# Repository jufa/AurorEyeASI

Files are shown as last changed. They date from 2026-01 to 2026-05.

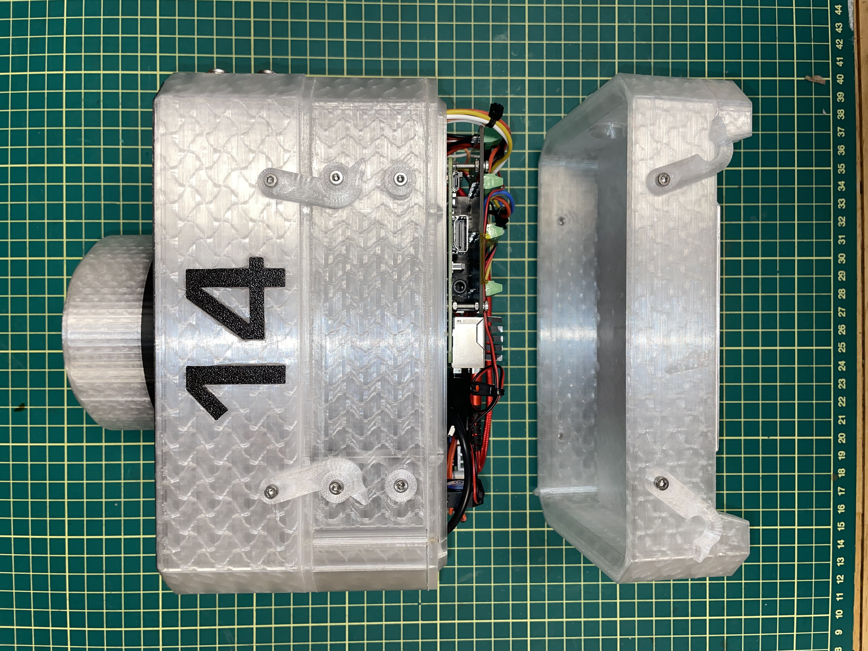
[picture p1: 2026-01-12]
BuildReferencePhotos/IMG_7756.jpg

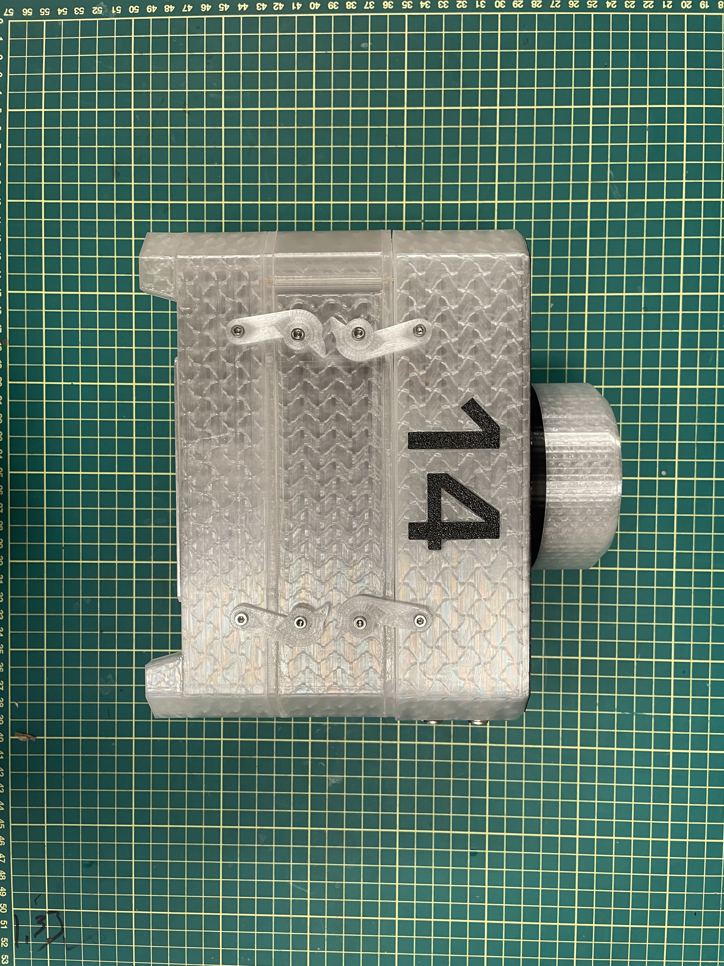
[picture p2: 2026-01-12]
BuildReferencePhotos/IMG_7746.jpg

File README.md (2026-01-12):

# AurorEyeASI
see [AurorEye.ca](https://auroreye.ca)

## Contact
jeremy@jufaintermedia.com or in this repository as an issue

## Terms of Use
Please see LICENSE.md

## Warranty
Please see LICENSE.md

### Bill of Materials
Please see BOM.md

## 3D Printable Shell
This repository includes an .3mf file for 3D printing. Preferred material is PETG.

## Development projects for students, researchers
### Hardware
* Low temperature tolerant LiFePO4 battery pack characterization
* Updates to KiCAD design files for Pi “HAT” circuit board
* Manufacturability considerations (maybe 3D printed internal frame for sensor alignment and support)
* Heat flow/moisture characterization and management (dew point, built-in heaters, condensation prevention for longer periods of deployment)
* 3D printed shell with in-built insulative properties, stackable, modular (in progress now)

### Optics and Sensor Characterization
* Optical characterization (lens, camera, distortion and light falloff parameters)
* Image file transforms (Camera internal color and post processing characterization)
* possible calibration with distortion from a weather cover dome

### Comms and UI
* Test with satellite or cellular Wifi
* Modify cloud upload for appropriate cloud environment (right now it is google cloud)
* UI development (currently a web app which provides flexibility as well as onboard buttons and display)
* Improvements or characterization of camera communication using established open source library (gPhoto2)

### Software/Firmware
* Onboard firmware updates, (branches off of main github repository with new features)
* Post processing tools updates (OpenCV, Python, Davinci Resolve Fusion workflows)
* Archiving, storing, and sharing system website (currently youtube and local backup servers of still image sequences)

### Skill areas for students
* Batteries and power electronics
* Temperature management hardware and sensing
* Magnetometers, Accelerometers for alignment
* Python programming
* Cloud API interface
* GitHub software collaboration
* Image processing and characterization using OpenCV or other open tools
* Image recognition/Machine Learning/AI
* 3D CAD/CAM
* Web Application development
* Video editing for outreach
* Field work campaigning and collaboration between multiple instruments
* Fabrication with Aluminum and Plastic
* Electronics assembly, packaging for harsh environments

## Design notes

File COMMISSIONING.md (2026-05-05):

1. Configure the camera as per camera_config/README.md
2. Check that software is running by turning on computer with our without camera connected. OLED should chow logho and boot sequence screen, finishing with a display of ISO and exposure time and GPS data
3. Verify GPS reporting on OLED
4. Verify accelerometer is reporting on the 'LEVEL' screen
5. Verfify camera can be powered up from the dummy battery
6. Verify camera is set to memory slot [M1] and camera configuration steps have been followed in /camera_setup
7. Power off system
8. Connect camera to the RPI via usb-C to usb-a cable
9. Ensure power switch on top of camera is set to ON
10. Power up computer and sensors
11. Check that camera is detected on OLED display (verify under 'SETTINGS' menu for a message like "NO ERRORS". If the camera is not detected, there will be a USB error message
12. Optional for debug/monitoring: inspect the log file using tail -f /mnt/extstore/auroreye_log.txt via your ssh connection to the unit
13. Wait for GPS time lock on main OLED status screen
14. Start a sequence using the START button and see if images are captured.
15. check that the sequence(s) are stored in /mnt/extstore as folders with the sequence start time: i.e. seq_YYYY-MM-DDTHH-MM-SS
16. From a remote computer you can select and download sequences using [https://github.com/jufa/AurorEyeASI/blob/main/tools/fetch_sequence.ssh] (Linux/Mac tested)

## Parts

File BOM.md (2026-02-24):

# Bill of Materials (BOM)
| Component                        | Qty | Description                                                                                                                                                                                                 |
|----------------------------------|-----|-------------------------------------------------------------------------------------------------------------------------------------------------------------------------------------------------------------|
| Ball head tripod with arca-swiss mount              | 1   | [Example](https://www.amazon.ca/dp/B0B1HYVVTV)   
| Camera                           | 1   | Sony ZV-E10 Mark I (Mark II is the current version, it is untested in this application at this time)                                                                                                       |
| Lens                             | 1   | Meike 6.5mm f/2.0 circular fisheye for Sony, [Example](https://www.amazon.ca/MEKE-Circular-Fisheye-Digital-Cameras) E-Mount                                                                                                                                                         |
| Controller                       | 1   | Raspberry Pi 3B+ (Pi 5 with NVME drive hat and cooling fan is an option too)                                                                                                                                          |
| OS Storage                       | 1   | 32GB MicroSD card, SanDisk 32GB Ultra or similar                                                                                                                                                           |
| External Storage                 | 1   | SanDisk 256GB Ultra Fit USB 3.1 Flash Drive - [SDCZ430-256G-G46](https://www.amazon.ca/dp/B07857Y17V)                                                                                                       |
| Hotspot WiFi                     | 1   | Optional. TP-Link USB A dongle (AC1300 chipset), e.g. TP-Link AC1300 USB WiFi Adapter (Archer T3U) or other AC1300-based dongle. one with an external antenna would be more useful fr increasing range                                                                                      |
| Accelerometer Board              | 1   | MPU-6050 Acceleration Sensor 3 axis with I2C interface – [Example](https://www.amazon.ca/dp/B07V67DQ5N)                       | GNSS/Magnetometer              | 1   | BN-880 with integrated HML5883 magnetometer - [Example](https://www.amazon.ca/dp/B086ZKFFY4)                                                                                                      |                                                                              |
| Interface                        | 4   | 12mm Momentary Push Button Switch – [Example](https://www.amazon.ca/dp/B0D874KSJ5)                                                                                                                         |
| Battery Pack                     | 1   | Talentcell LiFePo4 LF4100 battery pack, 76Wh                                                                                |
| 5A Rated Step-Down Converter     | 1   | [Example](https://www.amazon.ca/dp/B085T73CSD) or similar, used for powering the RPi                                    |
| Dummy Battery Pack Adapter       | 1   | Neewer DC Coupler Replacement for NP-FW50 Dummy Battery Power Adapter or similar                                                                                                                           |
| OLED Display                     | 1   | OLED 128x64 Pixel – I2C – 1.3 inch – SSD1306 or SH1106 – [Example](https://www.amazon.ca/dp/B07K7FZ9BZ)                                                                                                     |                                                                                                                                                          
| USB-C to USB-A Cable             | 1   | For camera/RPi interconnect, 18 inches or more                                                                                                                                                                                 |
| Ball Mount Tripod Interface      | 1   | 70mm Quick Release Plate Fits Arca-Swiss – [Example](https://www.amazon.ca/dp/B0725S67MM)                                                                                                                  |                                                                                                                           |
| Custom PCB Hat                   | 1   | Breakout for several I2C devices, UART; 2-layer PCB. Contact Repository Owner for this unpopulated board. COTS alternate: [Seeed Studio 103030275](https://www.digikey.ca/en/products/detail/seeed-technology-co-ltd/103030275/9771826)                         |
| Power cable for battery pack     | 1   | Male 4.0x1.7mm 90 Degree Angle Barrel Jack Power Cable with bare 2-wire at other end - [Example](https://www.amazon.ca/dp/B0D4J783D2) [DIGIKEY](https://www.digikey.com/en/products/detail/tensility-international-corp/053-0197R/568588) |
| terminal block accessories       | 1   | 5mm Pitch 2 Pin & 3 Pin PCB Mount Screw Terminal Block - [Example](https://www.amazon.ca/KeeYees-60pcs-Terminal-Connector-Arduino/dp/B07H5G7GC6) |
| Case, 3D Printed, PETG           | 1   | 3D printer capable of printing with 0.4mm nozzle diameter, 0.2-0.28mm layer height, PETG, example, Bambu labs A1 with default print plate and nozzle |
| Brass or aluminum wire, 3mm      | 1   | Approx 60mm for hinge pin |
| 1/8" aluminum      | 1   | Approx 120mm x 120mm for for base stiffening between arca swiss plate and bottom of shell |
| 22G wire      | 10'   | 22 Gauge multistrand with silicone insulation |
| 1/8" heatshrink      | 10"   |  |
| 3M doubleside foam tape      | 4"   |  |

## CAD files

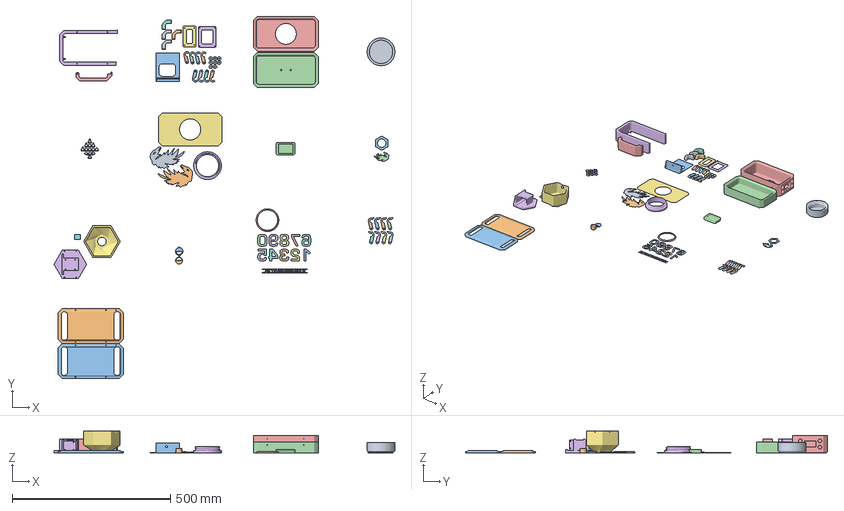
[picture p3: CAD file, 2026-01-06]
AurorEye-Complete-2026-01-06.3mf
1077.7 x 1144.3 x 69.0 mm
AurorEye3 case all.stl_5 x 4
AurorEye3 latch.stl_1 x 8
AurorEye3 latch.stl_2 x 8
AurorEye3 elec cover.stl
AurorEye3 lens ring.stl_1
AurorEye3 lens ring.stl_2
AurorEye3 blackout cover.stl
AurorEye3 cam bracket.stl_2
Lens_support_with_Arca_awiss.stl_Boolean
AurorEye3 door.stl
AurorEye3 electronics plates.stl_1
AurorEye3 electronics plates.stl_2
AUROREYEMINIv3.stl_2
AUROREYEMINIv3 top.stl_1
AUROREYEMINIv3 top.stl_2
AurorEye2 logo.stl_1 x 3
AUROREYEMINIv3 top.stl_1_A
AurorEye3 top cover.stl
AurorEye3 battery collar.stl_2_Boolean
AurorEye2 unit numberals.stl_1 x 2
AurorEye2 unit numberals.stl_2 x 2
AurorEye2 unit numberals.stl_3 x 2
AurorEye2 unit numberals.stl_4 x 2
AurorEye2 unit numberals.stl_5 x 2
AurorEye2 lens cap.stl_4
AurorEye3_plate.stl x 2
AurorEye3 wire clip.stl x 13
Cube_Boolean
AurorEye3-latch.stl_1 x 8
AurorEye3 vent.stl_1
AurorEye3 vent.stl_2

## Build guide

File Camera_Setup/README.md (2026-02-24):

# Camera Setup
The current version of AurorEye uses the Sony ZV-E10 Mark I camera.
This needs to have some default settings updated to work with the AurorEye software - specific settings that cannot be accessed from the USB control port, and are set up using the camera's on screen menu and back-of-camera buttons.

## Method 1: Copy predefined memory settings file onto SD card then into camera internal memory
0. Ensure camera is at latest Firmware version (2.0.2) [Link to firmware download](https://www.sony.ca/en/electronics/support/e-mount-body-zv-e-series/zv-e10/downloads). Note that the Sony Camera Driver may need to be updated on the host computer that is managing the firmware upgrade as per the instructions at the link
1. Copy the file `CAMPR01N.DAT` to an SD card under the folder path: `[SDCARD ROOT]/PRIVATE/SONY/SETTING/E10/CAMPR01N.DAT` NOTE: if your camera is set to PAL format for video, you may have to change the filename "N" to a "P" for the file to be recognized, or switch the camera to NTSC
3. Insert this SD card into the camera.
4. Make sure the USB-C cable is NOT connected to the camera
5. Power on the camera
6. In the camera menu, navigate to Tab 1, screen 3 `Shoot/Drive Mode`
7. Select item `Shoot Mode`
8. Select `MR1` aka `Recall Camera Set 1` from the vertical menu by pressing the roght side of the back-of-camera disc controller
9. you should see a grid of camera settings with tabs on top in this order `1`, `M1`, `M2` etc. Highlight the second tab labelled `M1`and press the center button. This sets the camera to the predefined settings that you copied to the SD card (good!)
10. This will kick you out into the schooting preview screen. Press the `Menu` Button on the back of the camera to get back to the menu screen on Tab 1, screen 3 `Shoot/Drive Mode`
11. Now navigate to the bottommost menu iem on the same screen: `Camera Set Memory`
12. Ensure the `1` tab on the top of this screen is highlighted (The leftmost tab, NOT `M1`)
13. Press the center button of the navigator ring on the back of camera. This should save the new settings to the INTERNAL memory slot of the Camera. The screen should say `Resgitered`
14. Now go to the top menu item `Shoot Mode` and this time change `M1` to `1` to tell the camera to boot up with these new settings which are now internal to the camera
15. This will kick us out back to the shoting preview/l;iveview screen. In the top left you should see a Camera Icon with a larger `M` to the right of it and a smaller `MR1` below it.
16. ***IMPORTANT STEP: REMOVE THE SD CARD***
17. Now the TOP of the camera: Ensure the camera switch is `ON` before mounting it into the AurorEye.
18. All done!

## Method 2: manually go through all menu screens and set them to match the PDF in this folder
Then save the settings using steps 10 onward above. This does not require you to copy the .DAT settings file to an SD card but can be tedious.

## Note on Sony behavior with saving 
in most cases you will be modifying the camera settings while the camera is connected to the AurorEye. The ZV-E10 has been characterized to determine it needs some time after it has been powered down via its own power switch to be sure any settings are saved.
 - make sure the AurorEye is done boot equence before changing settings
 - do not unpliug the USB cable when changing settings using camera controls and menu
 - ensure you save the settings once done to Camera Set Memory [1]
 - ensure the camera is using Recall Camera Settings [1]
 - after doing this, turn off the camera with its top plate on/off switch and wait 30 seconds to ensure settings are saved
 - power camera up again
 - now you can power off the AurorEye and the settings should be saved

## Notes on SD card parallel operation
In the case that you want to use your own workflow, you can save RAW file to an SD card inserted in the ZV-E10 with some precautions:
 - The SD card can fill up rapidly, the behaviour of the camera when SD card becaomes full while in capture sequence has not been tested
 - The settings for what files go to which storage media are under the camera menu "PC Remote Operation"

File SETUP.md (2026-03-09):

# Multistep commissioning

## Sub systems testing
Do these before interconnecting subsystems:
 - Keep buck converter output detached from all downstream electronics. Power up with 9VDC input voltage, adjust to output 5.2 VDC out.
 - Power up Raspberry Pi using a benchtop power supply or its USB power input. Attach HDMI Monitor and USB-A keyboard to note any errors during boot.
 - test camera with internal battery. Set menu system to allow 'PC Remote' access over USB as per [ZV-E10 manual](https://helpguide.sony.net/ilc/2070/v1/en/contents/TP0002392805.html)
 - test that camera dummy battery outputs 8.2 VDC when powered via its USB A input
 - test thaty dummey battery allows camera to power up Camera
 - leave camera top plate power switch to 'on'
 - attach camera to Pi via usb-C to usb-A data cable (not power-only; ensure data is supported)
   
## setting up SSH for network login:
run `./tools/pi-config/ssh_key_setup_run_once.sh` and follow instructions

# USB-A Thumb/SSD Drive
 - This may need to be mounted and formatted properly before the system can boot as each SSD drive has a different UUID at a OS level to mount successfully.
 - use `./tools/pi-config/setup_extstore.sh` tool to setup extstore with SSD thumbdrive installed in a USB port.

# I2C component tests
If RPI boots into command line, and you have logged in,:
enter into command line prompt:
`i2c-detect -y 1'
Look for these dvices to be listed in the detection grid:
```
0x1e - HMC5583 magnetometer built into BN-880 compass/GPS module OR:
0x0d - QMC5583 magnetometer if included as separate module board
0x3c - SSD1306 OLED display
0x68 - Accellerometer board
```

# GPS communication over serial
 - the GPS communicates over /dev/serial0 or /dev/ttyUSB0
 - check that `sudo tail -f /dev/ttyUSB0` or `sudo tail -f /dev/serial0` is relaying NMEA sentences, note that it may auto adapt its baud rate and return unparsable ASCII

# Camera detection
 - if booting succeeds, you can check if camera is detected:
 - command line: `gphoto2 --autot-detect` should list the ZV-E10 on a USB port

# AurorEye log file
 - the AurorEye software will attempt to log during boot to /mnt/extstore/auroreye_log.txt
 - `tail -f /mnt/extstore/auroreye_log.txt` in a separate terminal window to monitor errors and logging can help with comissioning and monitoring

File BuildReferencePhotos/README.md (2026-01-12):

# Build Reference Photos from Unit 14
Note that these are for reference only

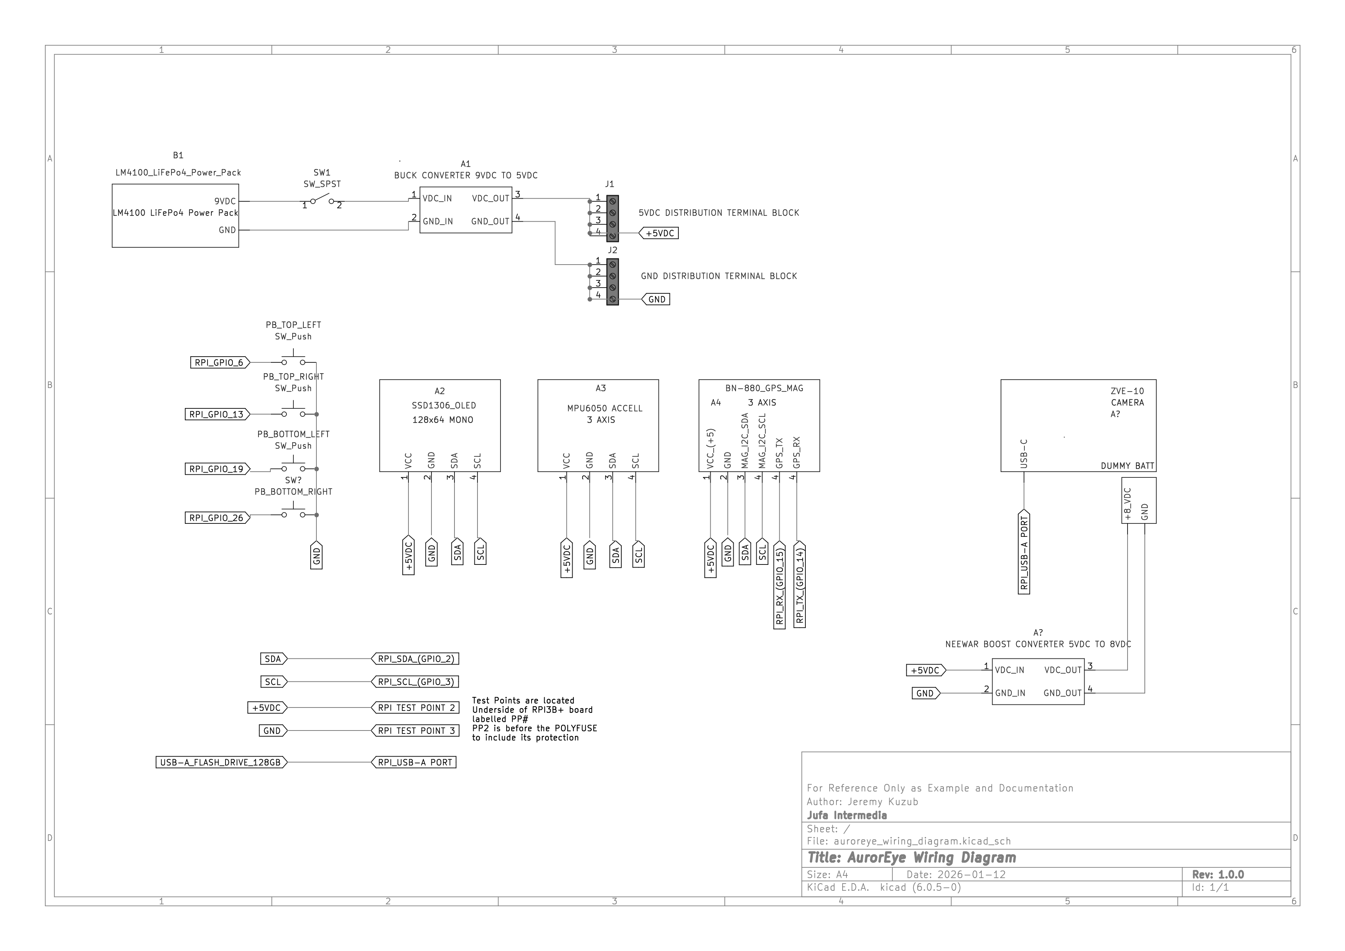
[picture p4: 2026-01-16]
auroreye_wiring_diagram_20260116.png

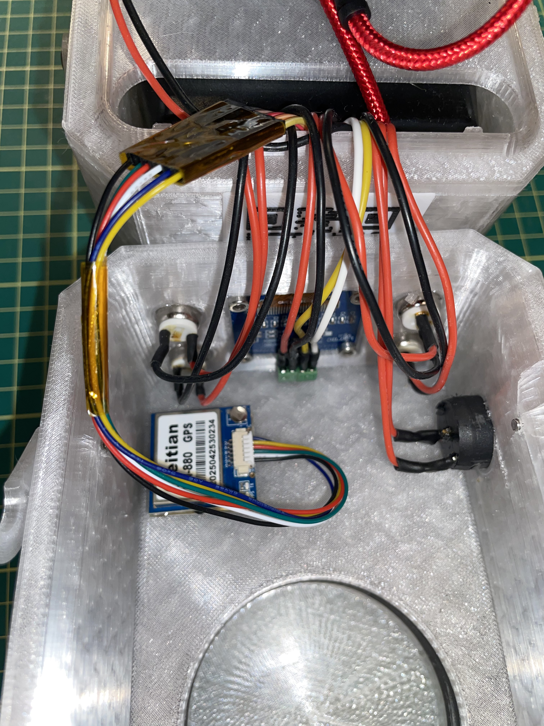
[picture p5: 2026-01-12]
BuildReferencePhotos/IMG_7755.jpg

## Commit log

2025-05-27 STL 3D print file for Shell/Case
    This replaces the Nanuk 904 OTS hard case, aluminum mount bracket with 3D printable Shell with stackable configurable trays for battery, electronics, camera, and interface. This design integrates a 1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
    [AurorEye Shell.stl]
2025-05-27 Update README.md
    add reference to STL 3D print file
2025-05-27 AurorEye Shell 3MF file
    for 3D printing
    [AurorEye Shell.3mf]
2025-10-30 Update README.md
    Update BOM with LiFePo battery and other Oct 2025 refinements
2025-11-01 Initial commit of camera setup folder
2025-11-01 Add ZVE10mkI camera setup DAT and PDF instructions
2026-01-06 Add latest 3D print files
    [AurorEye-Complete-2026-01-06.3mf]
2026-01-06 Delete AurorEye Shell.3mf
    deprecated 3D print file
    [AurorEye Shell.3mf]
2026-01-06 Delete AurorEye Shell.stl
    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
    [AurorEye Shell.stl]
2026-01-16 Update component wiring diagram reference
2026-02-17 Update camera settings file
2026-02-17 Revise camera setup instructions in README
    Updated instructions for copying settings file to SD card and saving camera settings.
2026-02-17 Include firmware update steps in README
    Added firmware update instructions for the Sony ZV-E10 camera.
2026-02-22 Update README with PAL format filename note
    Added note about filename change for PAL format cameras.
2026-02-24 Enhance README with notes on camera behavior
    Added notes on camera settings saving and SD card operation.
2026-02-24 Update note on Sony camera settings saving behavior
    Clarify the behavior of the ZV-E10 regarding settings saving after power down.
2026-02-24 Enhance power cable description with DIGIKEY link
    Updated the power cable entry to include an additional supplier link.
2026-03-09 Create SETUP.md with commissioning instructions
    Added detailed instructions for multistep commissioning, including subsystem testing, SSH setup, USB drive preparation, I2C tests, GPS communication, camera detection, and logging.
